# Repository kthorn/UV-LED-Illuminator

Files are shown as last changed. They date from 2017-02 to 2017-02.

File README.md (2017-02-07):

# UV LED Illuminator
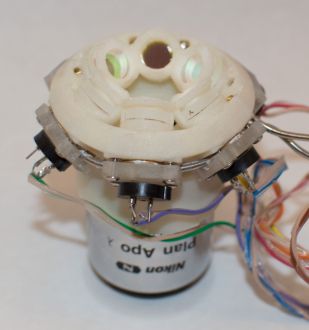
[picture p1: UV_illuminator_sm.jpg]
Image of Illuminator


This repository contains files for constructing an objective mounted UV epi-illuminator. It consists of six UV LEDs arranged around an objective to illuminate the focal plane. We have used it for excitation with 280 nm LEDs, but it can also be used for exciting fluorescence using visible wavelength LEDs. For UV LEDs the main advantage is that it does not require that the objective transmit the UV wavelengths for excitation. For visible LEDs it provides a simple and compact way to illuminate a sample that does not require a dichroic mirror or filter cube.

# What the files are
* [BillOfMaterials.txt: Parts list for project](BillOfMaterials.txt)
* 3D printed parts for the LED mount:
  * [4x LED ring light 2mm filter.ipt: LED mount that sits on a 4x/0.2 NA objective (Autocad Inventor format)](4x LED ring light 2mm filter.ipt)
  * [4x LED ring light 2mm filter.stl: same part, STL format](4x LED ring light 2mm filter.stl)
  * [LED cooling tubing cap 2.ipt: Clamps to hold the LEDs in place (Autocad Inventor format)](LED cooling tubing cap 2.ipt)
  * [LED cooling tubing cap 2.stl: same part, STL format](LED cooling tubing cap 2.stl)
* 3D printed parts for the water pump enclosure
  * [Pump enclosure MM0312.ipt: Enclosure to hold the water pump (Autocad Inventor format)](Pump enclosure MM0312.ipt)
  * [Pump enclosure MM0312.stl: same part, STL format](Pump enclosure MM0312.stl)
  * [Pump clamp MM0312.ipt: clamp to hold the water pump in place (Autocad Inventor format)](Pump clamp MM0312.ipt)
  * [Pump clamp MM0312.stl: same part, STL format](Pump clamp MM0312.stl)
  * [Pump lid MM0312.ipt: Pump enclosure lid (Autocad Inventor format)](Pump lid MM0312.ipt)
  * [Pump lid MM0312.stl: same part, STL format](Pump lid MM0312.stl)
* Other parts
  * [LED pump controller.ipt: Enclosure for the Arduino that controls the LEDs and water cooling pump (Autocad Inventor format)](LED pump controller.ipt)
  * [LED pump controller.stl: same part, STL format](LED pump controller.stl)
  * [LEDPumpController.ino: Arduino sketh for the pump controller](LEDPumpController.ino)

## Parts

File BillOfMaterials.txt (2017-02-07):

Part	Supplier	Part No.	Number	Unit	Cost	Total	Notes
Illuminator Assembly							
UV LED	Crystal IS	OPTAN280K	6	ea	$390.00 	"$2,340.00 "	
Bandpass Filters	Semrock	FF01-300/80-9-D	6	ea		"$1,401.95 "	
LED / Objective Mount	3D print		1	ea		$0.00 	
Plate to secure LED	Shapeways		6	ea	$6.50 	$39.00 	LED Cooling Tubing Cap 2 printed in frosted Ultra detail
0-80 Press fit inserts	McMaster-Carr	92395A109	1	pk	$8.50 	$8.50 	
0-80 screws	McMaster-Carr	92949A312	1	pk	$7.29 	$7.29 	
"Tubing for water cooling (1/16"" OD)"	McMaster-Carr	89895K611	1	foot	$9.94 	$9.94 	
Heat sink compund	McMaster-Carr	3883K24	1	tube	$11.70 	$11.70 	
							
LED Controller							
BNC Jack	Digi-Key	A32339-ND	1	ea	$2.81 	$2.81 	
Cable connector	Digi-Key	HPL14H-ND	1	ea	$3.62 	$3.62 	
IDC connector	Digi-Key	HKC14S-ND	3	ea	$0.44 	$1.32 	
Jack for pump	Digi-Key	CP-6-ND	2	ea	$2.33 	$4.66 	
ProtoShield	Sparkfun	DEV-07914	1	ea	$9.95 	$9.95 	
MOSFET 60V 30A	Sparkfun	COM-10213	2	ea	$0.95 	$1.90 	
Arduino Uno	Sparkfun	DEV-11021	1	ea	$29.95 	$29.95 	
12V Power Supply	Sparkfun	TOL-11296	1	ea	$9.95 	$9.95 	
Molex socket						$0.00 	Cut up disk drive cable from PC power supply
10 kOhm resistor			2	ea			
39 Ohm resistor			6	ea			
4-40 Press-in insert	McMaster-Carr	92395A315	1	pk	$6.50 	$6.50 	
4-40 screws						$0.00 	
Small piece of flat ribbon cable						$0.00 	
Housing	3D print					$0.00 	
							
Cable to LEDs							
Ribbon cable	Digi-Key	MC14F-10-ND	1	10'	$9.97 	$9.97 	
LED connectors	Digi-Key	ED2150-ND	6	ea	$1.52 	$9.12 	
							
Pump							
Housing	3D print					$0.00 	
Pump	Simply Pumps	MM0312	1	ea	$34.00 	$34.00 	
Cable to Arduino	Digi-Key	839-1008-ND	1	ea	$5.50 	$5.50 	
"Panel Mount Female Luer x 1/8"" barb"	Value Plastics	FTLLB230-1	1	pk/100	$30.40 	$30.40 	
Nuts for Luer	McMaster-Carr	94812A117	1	pk	$6.09 	$6.09 	
Bottle	VWR	16125-107	1	pk/6	$111.57 	$111.57 	
"1/8"" barb x Male Luer"	Value Plastics	MTLL230-9	1	pk/100	$18.90 	$18.90 	
"1/8"" Tygon tubing"						$0.00

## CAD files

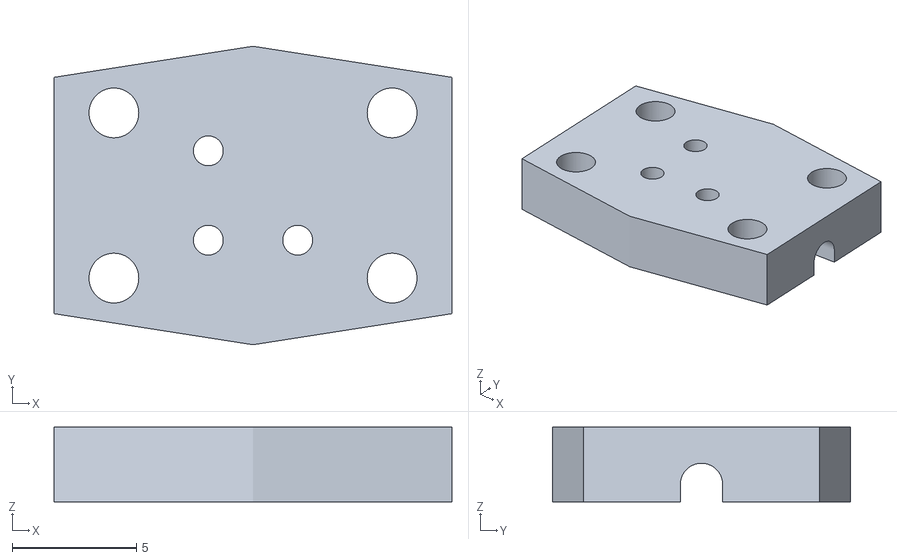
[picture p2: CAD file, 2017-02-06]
LED cooling tubing cap 2.stl
16.0 x 12.0 x 3.00

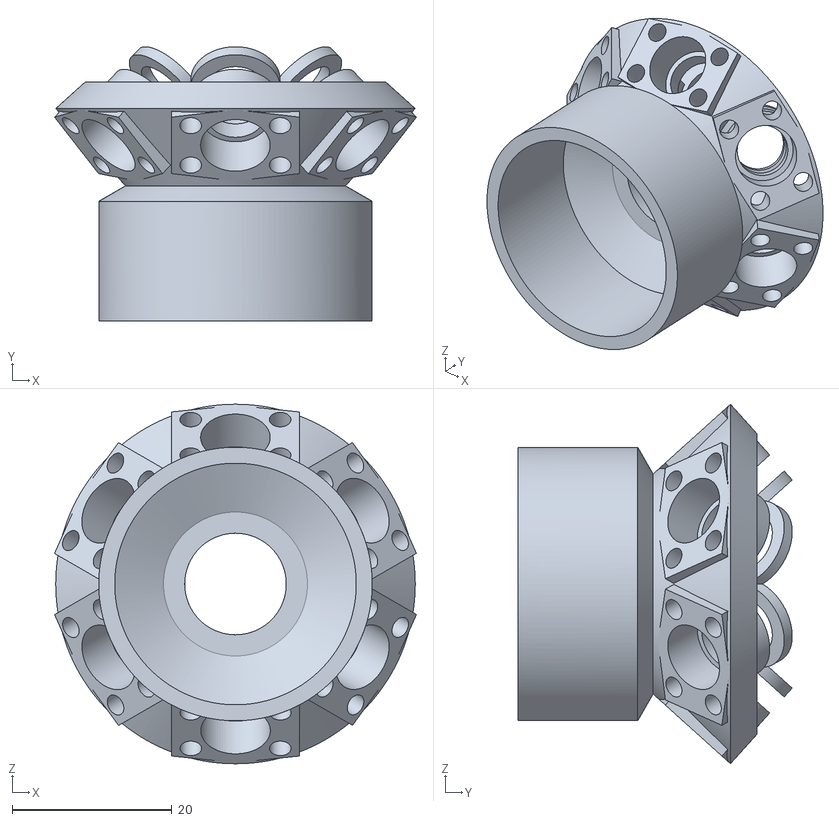
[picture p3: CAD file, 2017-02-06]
4x LED ring light 2mm filter.stl
45.3 x 34.3 x 45.0

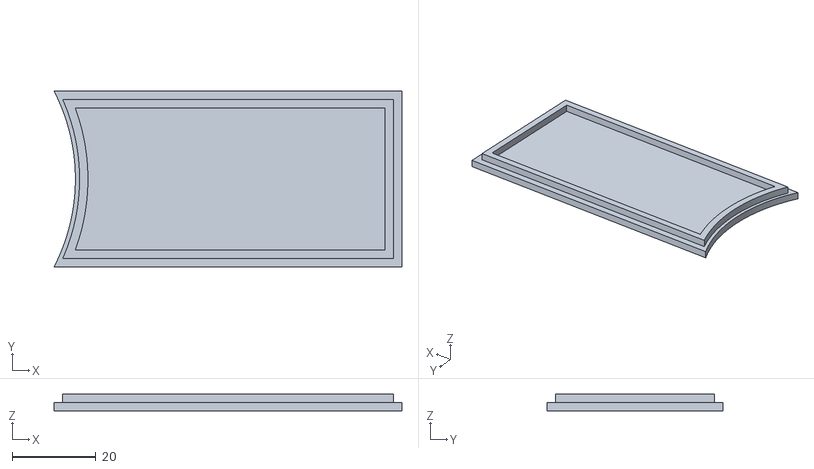
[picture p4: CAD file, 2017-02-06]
Pump lid MM0312.stl
83.1 x 42.0 x 4.00

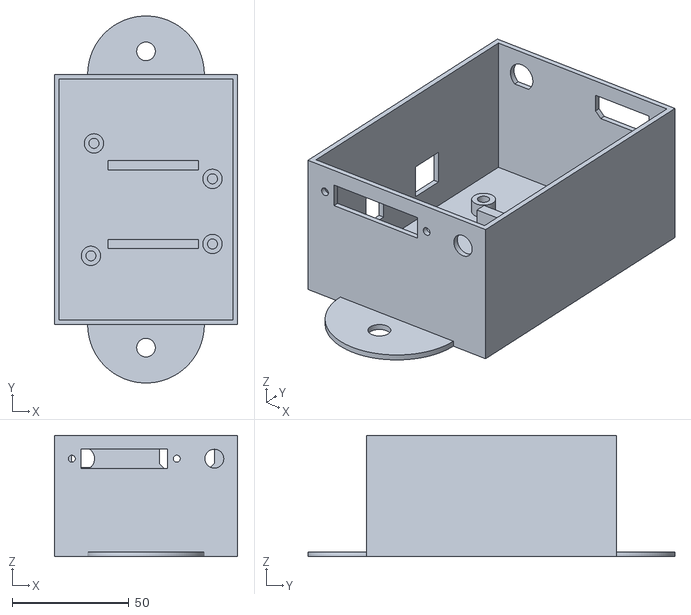
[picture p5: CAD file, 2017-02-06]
LED pump controller.stl
78.6 x 157.3 x 52.0

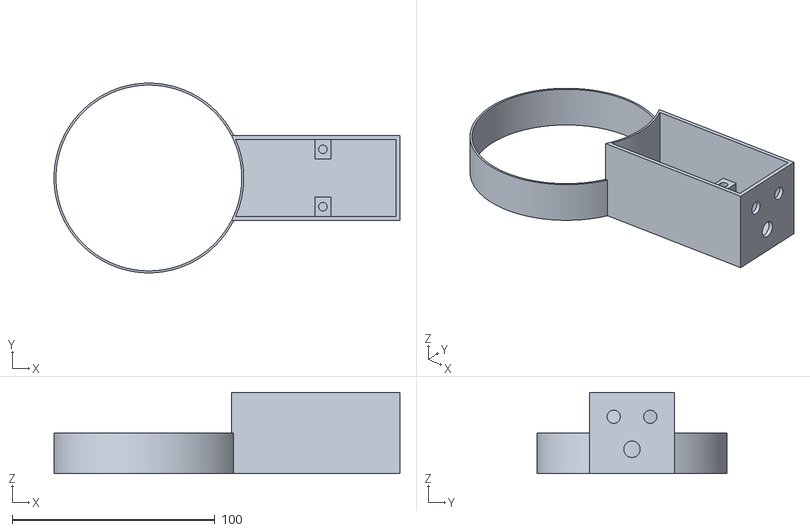
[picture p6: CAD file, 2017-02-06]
Pump enclosure MM0312.stl
170.5 x 93.5 x 40.0

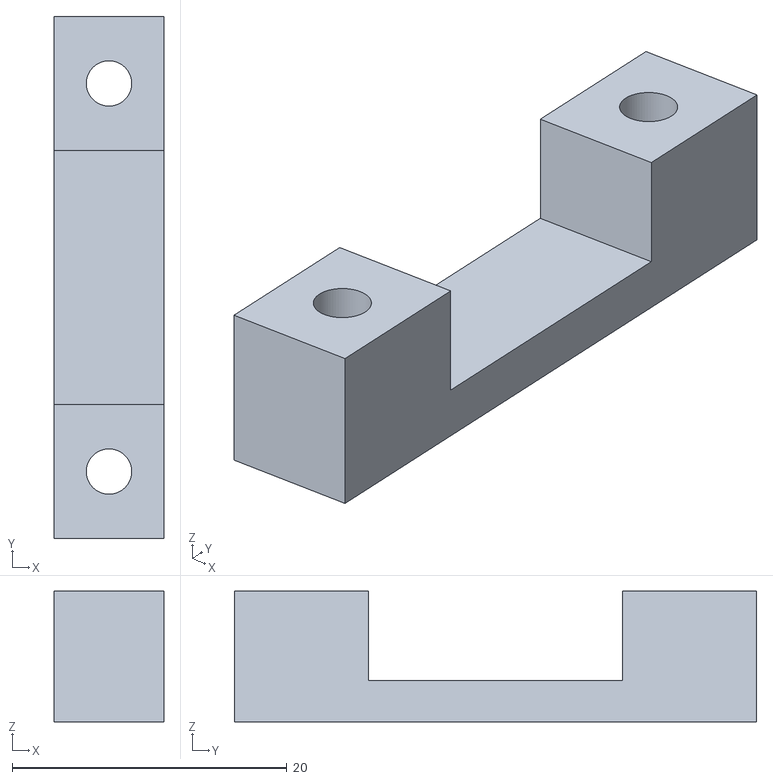
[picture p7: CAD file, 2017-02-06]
Pump clamp MM0312.stl
8.00 x 38.0 x 9.50

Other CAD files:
4x LED ring light 2mm filter.ipt
LED cooling tubing cap 2.ipt
LED pump controller.ipt
Pump clamp MM0312.ipt
Pump enclosure MM0312.ipt
Pump lid MM0312.ipt

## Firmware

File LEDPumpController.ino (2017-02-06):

/*
 * This goal of the application is to set the digital output on pins 8-13 
 * This can be accomplished in three ways.  First, a serial command can directly set
 * the digital output pattern.  Second, a series of patterns can be stored in the 
 * Arduino and TTLs coming in on pin 2 will then trigger to the consecutive pattern (trigger mode).
 * Third, intervals between consecutive patterns can be specified and paterns will be 
 * generated at these specified time points (timed trigger mode).
 *
 * Interface specifications:
 * digital pattern specification: single byte, bit 0 corresponds to pin 8, 
 *   bit 1 to pin 9, etc..  Bits 7 and 8 will not be used (and should stay 0).
 *
 * Set digital output command: 1p
 *   Where p is the desired digital pattern.  Controller will return 1 to 
 *   indicate succesfull execution.
 *
 * Get digital output command: 2
 *   Controller will return 2p.  Where p is the current digital output pattern
 *
 * Set Analogue output command: 3xvv
 *   Where x is the output channel (either 1 or 2), and vv is the output in a 
 *   12-bit significant number.
 *   Controller will return 3xvv:
 *
 * Get Analogue output:  4
 *
 *
 * Set digital patten for triggered mode: 5xd 
 *   Where x is the number of the pattern (currently, 12 patterns can be stored).
 *   and d is the digital pattern to be stored at that position.  Note that x should
 *   be the real number (i.e., not  ASCI encoded)
 *   Controller will return 5xd 
 *
 * Set the Number of digital patterns to be used: 6x
 *   Where x indicates how many digital patterns will be used (currently, up to 12
 *   patterns maximum).  In triggered mode, after reaching this many triggers, 
 *   the controller will re-start the sequence with the first pattern.
 *   Controller will return 6x
 *
 * Skip trigger: 7x
 *   Where x indicates how many digital change events on the trigger input pin
 *   will be ignored.
 *   Controller will respond with 7x
 *
 * Start trigger mode: 8
 *   Controller will return 8 to indicate start of triggered mode
 *   Stop triggered a 9. Trigger mode will  supersede (but not stop) 
 *   blanking mode (if it was active)
 * 
 * Stop Trigger mode: 9
 *   Controller will return 9x where x is the number of triggers received during the last
 *   trigger mode run
 *
 * Set time interval for timed trigger mode: 10xtt
 *   Where x is the number of the interval (currently, 12 intervals can be stored)
 *   and tt is the interval (in ms) in Arduino unsigned int format.  
 *   Controller will return 10x
 *
  * Sets how often the timed pattern will be repeated: 11x
 *   This value will be used in timed-trigger mode and sets how often the output
 *   pattern will be repeated. 
 *   Controller will return 11x
 *  
 * Starts timed trigger mode: 12
 *   In timed trigger mode, digital patterns as set with function 5 will appear on the 
 *   output pins with intervals (in ms) as set with function 10.  After the number of 
 *   patterns set with function 6, the pattern will be repeated for the number of times
 *   set with function 11.  Any input character (which will be processed) will stop 
 *   the pattern generation.
 *   Controller will retun 12.
 * 
 * Start blanking Mode: 20
 *   In blanking mode, zeroes will be written on the output pins when the trigger pin
 *   is low, when the trigger pin is high, the pattern set with command #1 will be 
 *   applied to the output pins. 
 *   Controller will return 20
 *
 * Stop blanking Mode: 21
 *   Stops blanking mode.  Controller returns 21
 *
 * Blanking mode trigger direction: 22x
 *   Sets whether to blank on trigger high or trigger low.  x=0: blank on trigger high,
 *   x=1: blank on trigger low.  x=0 is the default
 *   Controller returns 22
 *
 * 
 * Get Identification: 30
 *   Returns (asci!) MM-Ard\r\n
 *
 * Get Version: 31
 *   Returns: version number (as ASCI string) \r\n
 *
 * Read digital state of analogue input pins 0-5: 40
 *   Returns raw value of PINC (two high bits are not used)
 *
 * Read analogue state of pint pins 0-5: 41x
 *   x=0-5.  Returns analogue value as a 10-bit number (0-1023)
 *
 *
 * 
 * Possible extensions:
 *   Set and Get Mode (low, change, rising, falling) for trigger mode
 *   Get digital patterm
 *   Get Number of digital patterns
 */
 
   unsigned int version_ = 2;
   
   // pin on which to receive the trigger (2 and 3 can be used with interrupts, although this code does not use interrupts)
   int inPin_ = 2;
   // to read out the state of inPin_ faster, use 
   int inPinBit_ = 1 << inPin_;  // bit mask 
   
   // pin connected to DIN of TLV5618
   int dataPin = 3;
   // pin connected to SCLK of TLV5618
   int clockPin = 4;
   // pin connected to CS of TLV5618
   int latchPin = 5;

   const int SEQUENCELENGTH = 12;  // this should be good enough for everybody;)
   byte triggerPattern_[SEQUENCELENGTH] = {0,0,0,0,0,0,0,0,0,0,0,0};
   unsigned int triggerDelay_[SEQUENCELENGTH] = {0,0,0,0,0,0,0,0,0,0,0,0};
   int patternLength_ = 0;
   byte repeatPattern_ = 0;
   volatile int triggerNr_; // total # of triggers in this run (0-based)
   volatile int sequenceNr_; // # of trigger in sequence (0-based)
   int skipTriggers_ = 0;  // # of triggers to skip before starting to generate patterns
   byte currentPattern_ = 0;
   const unsigned long timeOut_ = 1000;
   bool blanking_ = false;
   bool blankOnHigh_ = false;
   bool triggerMode_ = false;
   boolean triggerState_ = false;
   
   //Variables for added pump control
   unsigned long startMillis;
   const unsigned long waitTime = 15000;
   int pumpState;
   int LEDstate;
   const int pumpPin = 7;
 
 void setup() {
   // Higher speeds do not appear to be reliable
   Serial.begin(57600);
  
   pinMode(inPin_, INPUT);
   pinMode (dataPin, OUTPUT);
   pinMode (clockPin, OUTPUT);
   pinMode (latchPin, OUTPUT);
   pinMode(8, OUTPUT);
   pinMode(9, OUTPUT);
   pinMode(10, OUTPUT);
   pinMode(11, OUTPUT);
   pinMode(12, OUTPUT);
   pinMode(13, OUTPUT);
   
   pinMode(pumpPin, OUTPUT);
   
   // Set analogue pins as input:
   DDRC = DDRC & B11000000;
   // Turn on build-in pull-up resistors
   PORTC = PORTC | B00111111;
   
   digitalWrite(latchPin, HIGH);   
 }
 
 void loop() {
   if (Serial.available() > 0) {
     int inByte = Serial.read();
     switch (inByte) {
       
       // Set digital output
       case 1 :
          if (waitForSerial(timeOut_)) {
            currentPattern_ = Serial.read();
            // Do not set bits 6 and 7 (not sure if this is needed..)
            currentPattern_ = currentPattern_ & B00111111;
            if (!blanking_)
              PORTB = currentPattern_;
            Serial.write( byte(1));
          }
          break;
          
       // Get digital output
       case 2:
          Serial.write( byte(2));
          Serial.write( PORTB);
          break;
          
       // Set Analogue output (TODO: save for 'Get Analogue output')
       case 3:
         if (waitForSerial(timeOut_)) {
           int channel = Serial.read();
           if (waitForSerial(timeOut_)) {
              byte msb = Serial.read();
              msb &= B00001111;
              if (waitForSerial(timeOut_)) {
                byte lsb = Serial.read();
                analogueOut(channel, msb, lsb);
                Serial.write( byte(3));
                Serial.write( channel);
                Serial.write(msb);
                Serial.write(lsb);
              }
           }
         }
         break;
         
       // Sets the specified digital pattern
       case 5:
          if (waitForSerial(timeOut_)) {
            int patternNumber = Serial.read();
            if ( (patternNumber >= 0) && (patternNumber < SEQUENCELENGTH) ) {
              if (waitForSerial(timeOut_)) {
                triggerPattern_[patternNumber] = Serial.read();
                triggerPattern_[patternNumber] = triggerPattern_[patternNumber] & B00111111;
                Serial.write( byte(5));
                Serial.write( patternNumber);
                Serial.write( triggerPattern_[patternNumber]);
                break;
              }
            }
          }
          Serial.write( "n:");//Serial.print("n:");
          break;
          
       // Sets the number of digital patterns that will be used
       case 6:
         if (waitForSerial(timeOut_)) {
           int pL = Serial.read();
           if ( (pL >= 0) && (pL <= 12) ) {
             patternLength_ = pL;
             Serial.write( byte(6));
             Serial.write( patternLength_);
           }
         }
         break;
         
       // Skip triggers
       case 7:
         if (waitForSerial(timeOut_)) {
           skipTriggers_ = Serial.read();
           Serial.write( byte(7));
           Serial.write( skipTriggers_);
         }
         break;
         
       //  starts trigger mode
       case 8: 
         if (patternLength_ > 0) {
           sequenceNr_ = 0;
           triggerNr_ = -skipTriggers_;
           triggerState_ = digitalRead(inPin_) == HIGH;
           PORTB = B00000000;
           Serial.write( byte(8));
           triggerMode_ = true;           
         }
         break;
         
         // return result from last triggermode
       case 9:
          triggerMode_ = false;
          PORTB = B00000000;
          Serial.write( byte(9));
          Serial.write( triggerNr_);
          break;
          
       // Sets time interval for timed trigger mode
       // Tricky part is that we are getting an unsigned int as two bytes
       case 10:
          if (waitForSerial(timeOut_)) {
            int patternNumber = Serial.read();
            if ( (patternNumber >= 0) && (patternNumber < SEQUENCELENGTH) ) {
              if (waitForSerial(timeOut_)) {
                unsigned int highByte = 0;
                unsigned int lowByte = 0;
                highByte = Serial.read();
                if (waitForSerial(timeOut_))
                  lowByte = Serial.read();
                highByte = highByte << 8;
                triggerDelay_[patternNumber] = highByte | lowByte;
                Serial.write( byte(10));
                Serial.write(patternNumber);
                break;
              }
            }
          }
          break;

       // Sets the number of times the patterns is repeated in timed trigger mode
       case 11:
         if (waitForSerial(timeOut_)) {
           repeatPattern_ = Serial.read();
           Serial.write( byte(11));
           Serial.write( repeatPattern_);
         }
         break;

       //  starts timed trigger mode
       case 12: 
         if (patternLength_ > 0) {
           PORTB = B00000000;
           Serial.write( byte(12));
           for (byte i = 0; i < repeatPattern_ && (Serial.available() == 0); i++) {
             for (int j = 0; j < patternLength_ && (Serial.available() == 0); j++) {
               PORTB = triggerPattern_[j];
               delay(triggerDelay_[j]);
             }
           }
           PORTB = B00000000;
         }
         break;

       // Blanks output based on TTL input
       case 20:
         blanking_ = true;
         Serial.write( byte(20));
         break;
         
       // Stops blanking mode
       case 21:
         blanking_ = false;
         Serial.write( byte(21));
         break;
         
       // Sets 'polarity' of input TTL for blanking mode
       case 22: 
         if (waitForSerial(timeOut_)) {
           int mode = Serial.read();
           if (mode==0)
             blankOnHigh_= true;
           else
             blankOnHigh_= false;
         }
         Serial.write( byte(22));
         break;
         
       // Gives identification of the device
       case 30:
         Serial.println("MM-Ard");
         break;
         
       // Returns version string
       case 31:
         Serial.println(version_);
         break;
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

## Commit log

2017-02-07 Updates to Readme
    Converted BillOfMaterials to text file, added image of illuminator.
    [BillOfMaterials.xlsx]
2017-02-07 Added filters to bill of materials
